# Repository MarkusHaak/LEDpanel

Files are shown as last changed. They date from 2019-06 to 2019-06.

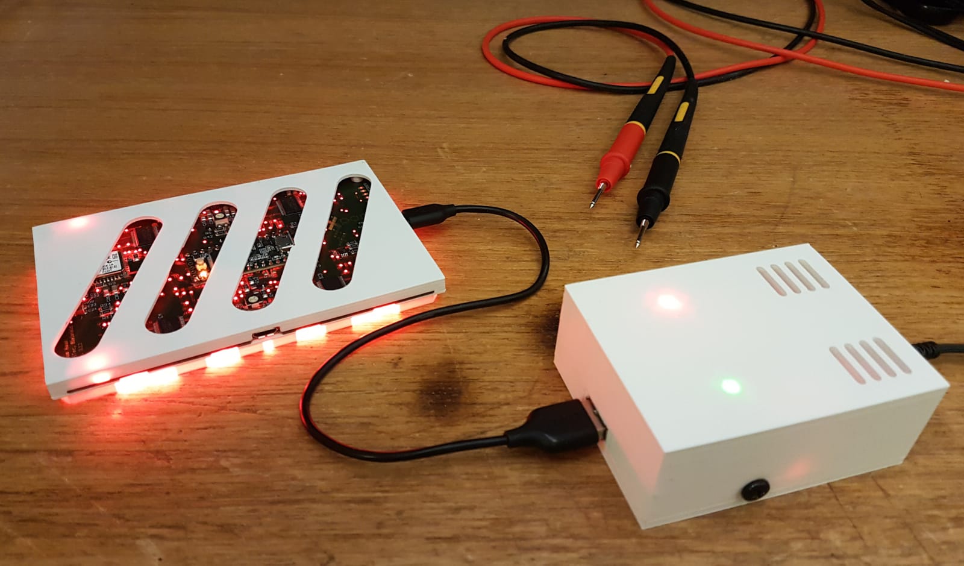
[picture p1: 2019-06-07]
preview/7.jpeg

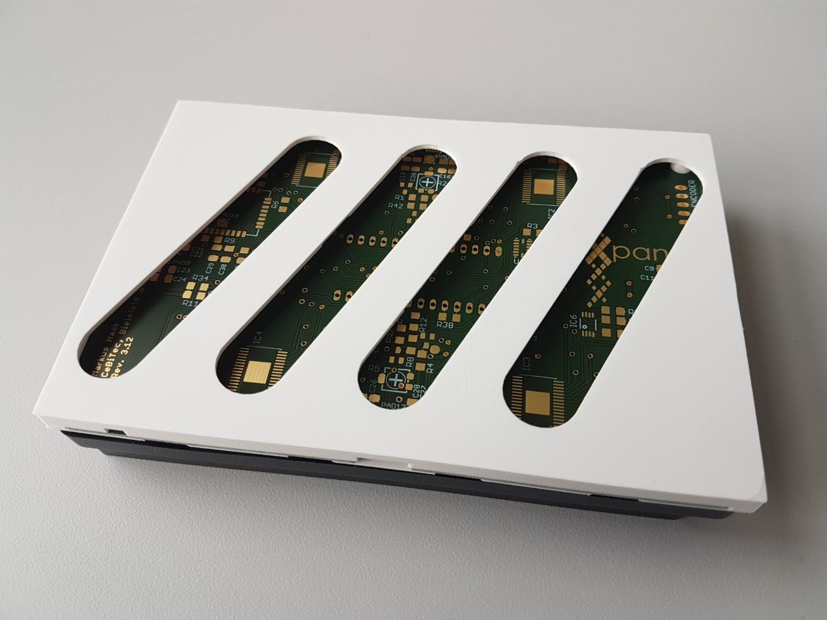
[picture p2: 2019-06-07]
preview/5.jpeg

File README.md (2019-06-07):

# LEDpanel
A multifunctional, bluetooth controlled LED panel for illuminating 96-well microtiter plates containing biological or chemical samples. The first version of this hardware was developed as part of the iGEM project from team Bielefeld CeBiTec 2017. For a detailed description of this first model and its applications in our project, see the [Hardware page](2017.igem.org/Team:Bielefeld-CeBiTec/Hardware) of our project wiki.

## Disclaimer

The hardware described on this github repository is still in prototype phase and both software and hardware may contain design faults. Furthermore, I do not take any responsibility and I am not liable for any damage that is caused by handling of electrical components or devices based on designs, instructions and information in this repository.

## Some Hints for Assembly

This repository is new and there is a lack of documentation. Until I find the time to write a comprehensive instruction for assembly and usage, the following hints are intended to give some orientation.

* In principal, any LEDs can be mounted on the LED panel. The constant current flowing through the LEDs is adjustable with potentiometers on the PCB itself. The LED panel is designed to be configurable to either control the current of all LEDs with a single potentiometer, or two groups of LEDs with an individual potentiometer for each group. Therefore, it is possible to mount two different groups of LEDs on the LED panel. In any case, I highly recommend to adapt the footprint in the PCB design files according to the instructions in the LED's technical sheets.

* Please adapt the file "model_slim_microtiter_adapter.stl" to fit the micro titer plates that are used in your laboratory.

* The parts list is outdated and is probably missing some required parts. Anyways, it might give some orientation in choosing the right parts.

* The LED panel requires two different voltages supplied over a micro usb cable: 3.3 V for the micro controller and logic, and a seperate LED supply voltage that should be at least 0.4 volts above the supply voltage of the LEDs in use. I used two LM2596 based DC-DC voltage regulator boards in a seperate 3d printed case (voltage_regulators_case.stl) to supply the required voltages from a standard 5V DC mains adapter with a barrel connector.

* The LED panel is intended to be controlled over bluetooth via an Android application. Nevertheless, some gpio pins of the teensy are traced to the side of the PCB for optional soldering of pin headers to the PCB that allow the connection of a small LCD screen and a rotary encoder to control basic functionalities of the LED panel. If this is intended, the Arduino code will probably need to be revised. In addition, the 3d printed case needs to be modified accordingly to create space for the display and the rotary encoder.

* The supplied .stl files are solely for illumination of micro titer plates from beneath. For illumination from above a plate, a different 3d printed microtiter adapter needs to be designed.

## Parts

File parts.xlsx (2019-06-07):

class | value | package | distributor | ID | link | # order | p.P. | sum / €
 |  |  |  |  |  |  |  | 0
capacitors | 100n | C1206 | Mouser | 77-VJ1206Y104KXXPBC | https://www.mouser.de/ProductDetail/Vishay-Vitramon/VJ1206Y104KXXPW1BC | 50 | 0.027 | 1.35
 | 10u/16V | C1206 | Mouser | 581-1206ZC106MAT2A | https://www.mouser.de/ProductDetail/AVX/1206ZC106MAT2A | 10 | 0.162 | 1.62
 | 100u/6V3 | C1206 | Mouser | 810-C3216X5R0J107M | https://www.mouser.de/ProductDetail/TDK/C3216X5R0J107M160AB | 10 | 0.845 | 8.45
 |  |  |  |  |  |  |  | 0
pinheaders | female | 18 | Mouser | 437-8018701810001101 | https://www.mouser.de/ProductDetail/Preci-dip/801-87-018-10-001101 | 2 | 1.18 | 2.36
 |  |  |  |  |  |  |  | 0
PWM driver | TLC5947-DAP | HTSSOP32DAP | Mouser | 595-TLC5947DAPR | https://www.mouser.de/ProductDetail/Texas-Instruments/TLC5947DAPR?qs=sGAEpiMZZMsE420DPIasPoaSsRjR8BzZEcbKcRNRsRk%3d | 5 | 2.87 | 14.35
 |  |  |  |  |  |  |  | 0
sensors | MCP9808 | MSOP8 | Mouser | 579-MCP9808T-E/MS | https://www.mouser.de/ProductDetail/Microchip-Technology/MCP9808T-E-MS | 3 | 1.12 | 3.36
 | ADXL345BCCZ | LGA14R80P3X6_300X500X100 | Mouser | 584-ADXL345BCCZ | https://www.mouser.de/ProductDetail/Analog-Devices/ADXL345BCCZ?qs=sGAEpiMZZMvwE4h8i4g3cmpdANGD53Y62K0svRyi38E%3d | 2 | 5.69 | 11.38
 |  |  |  |  |  |  |  | 0
USB | USB3065-XX-00-A_REVE | GCT_USB3065-XX-00-A_REVE | Mouser | 629105136821 | https://www.mouser.de/ProductDetail/Wurth-Electronics/629105136821 | 6 | 1.11 | 6.66
 |  |  |  |  |  |  |  | 0
LED | KPT-1608LVSECK-J3-PRV | KINGBRIGHT_1.6X0.8 | Mouser | APT1608LSECK/J3-PRV | https://www.mouser.de/ProductDetail/Kingbright/APT1608LSECK-J3-PRV | 5 | 0.402 | 2.01
 | KPT-1608LVZGCK | KINGBRIGHT_1.6X0.8 | Mouser | APT1608LZGCK | https://www.mouser.de/ProductDetail/Kingbright/APT1608LZGCK | 5 | 0.41 | 2.05
 | VLMU1610-365-135 | PLCC-2 | Mouser | 78-VLMR333U1AA-GS08 | https://www.mouser.de/ProductDetail/Vishay-Semiconductors/VLMR333U1AA-GS08 | 130 | 0.305 | 39.65
 |  |  |  |  |  |  |  | 0
transistors | BC807-16SMD | SOT23-BEC | Mouser | 863-BC807-25LT3G | https://www.mouser.de/ProductDetail/ON-Semiconductor/BC807-25LT3G | 3 | 0.098 | 0.294
 |  |  |  |  |  |  |  | 0
resistors | 1K | R1206 | Mouser | 71-RCG12061K00FKEA | https://www.mouser.de/ProductDetail/Vishay-Draloric/RCG12061K00FKEA | 10 | 0.082 | 0.82
 | 10K | R1206 | Mouser | 71-RCG120610K0FKEA | https://www.mouser.de/ProductDetail/Vishay-Draloric/RCG120610K0FKEA | 15 | 0.082 | 1.23
 | 4K7 | R1206 | Mouser | 71-RCG12064K70JNEA | https://www.mouser.de/ProductDetail/Vishay-Draloric/RCG12064K70JNEA | 5 | 0.082 | 0.41
 | 0R | R1206 | Mouser | 71-RCG12060000Z0EA | https://www.mouser.de/ProductDetail/Vishay-Draloric/RCG12060000Z0EA | 15 | 0.082 | 1.23
 | 750R | R1206 | Mouser | 603-RC1206FR-07750RL | https://www.mouser.de/ProductDetail/Yageo/RC1206FR-07750RL | 10 | 0.02 | 0.2
 | 330R | R1206 | Mouser | 603-RC1206FR-07330RL | https://www.mouser.de/ProductDetail/Yageo/RC1206FR-07330RL?qs=sGAEpiMZZMvdGkrng054t8AJgcdMkx7xi3kA7AOJ26Y%3d | 10 | 0.02 | 0.2
 | 5K TRIMM | RTRIM4G/J | Mouser | 72-TS53YJ-5K | https://www.mouser.de/ProductDetail/Vishay-Sfernice/TS53YJ502MR10 | 4 | 1.06 | 4.24
 |  |  |  |  |  |  |  | 0
bluetooth | BLUETOOTH-RN-41" | RN41 | Mouser | 765-RN-41 | https://www.mouser.de/ProductDetail/Microchip-Technology/RN41-I-RM?qs=sGAEpiMZZMtqO%252bWUGLBzeMW4TCGBne5E | 1 | 21.35 | 21.35
 |  |  |  |  |  |  |  | 0
microcontroller | teensy3.2 |  | Mouser | 474-DEV-13736 | https://www.mouser.de/ProductDetail/SparkFun/DEV-13736 | 1 | 19.19 | 19.19
 |  |  |  |  |  |  |  | 0
PCB | PCB 127.76 x 85,48 |  | BETA Layout |  | https://de.beta-layout.com/leiterplatten/konfigurator/ | 1 | 84.9 | 84.9
 |  |  |  |  |  |  |  | 0
3D printing filament | PLA 1.75mm white |  | Conrad | 1093139 | https://www.conrad.de/de/filament-renkforce-pla-175-mm-weiss-1-kg-1093139.html | 1 | 32.99 | 32.99
 |  |  |  |  |  |  |  | 0
voltage regulators | LM2596 (or equivalent) DC DC voltage regulator boards |  | amazon |  | https://www.amazon.de/WINOMO-1-23-30V-DC-Einstellbare-Spannung-Konverter/dp/B01B7EEWGK?__mk_de_DE=%C3%85M%C3%85%C5%BD%C3%95%C3%91&s=gateway | 5 |  | 12.39

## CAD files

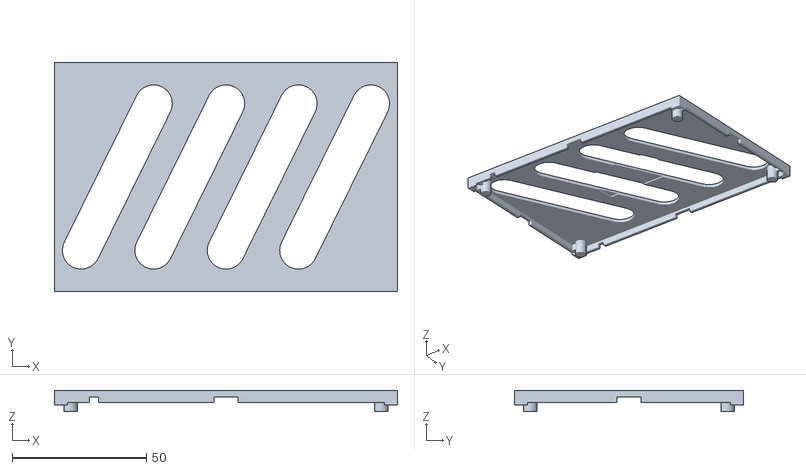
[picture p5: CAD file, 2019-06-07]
case/model_slim_lower_case.stl
127.8 x 85.5 x 8.00

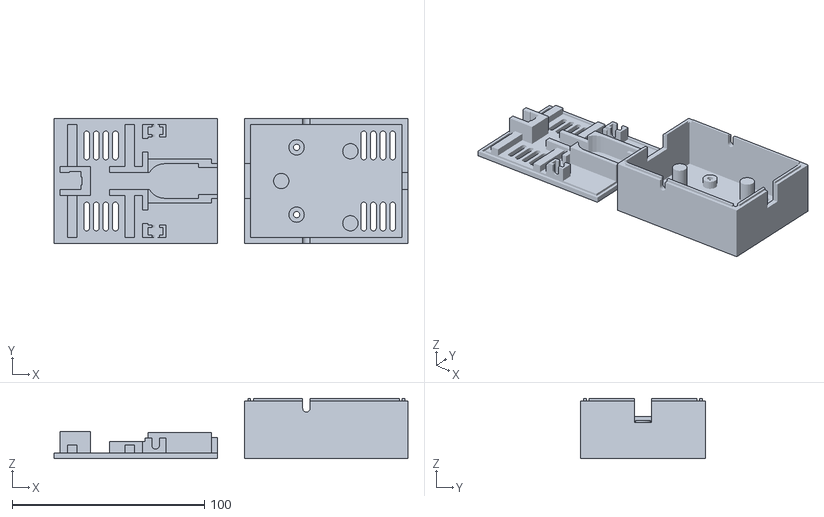
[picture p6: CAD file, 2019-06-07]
case/voltage_regulators_case.stl
184.3 x 65.0 x 31.3

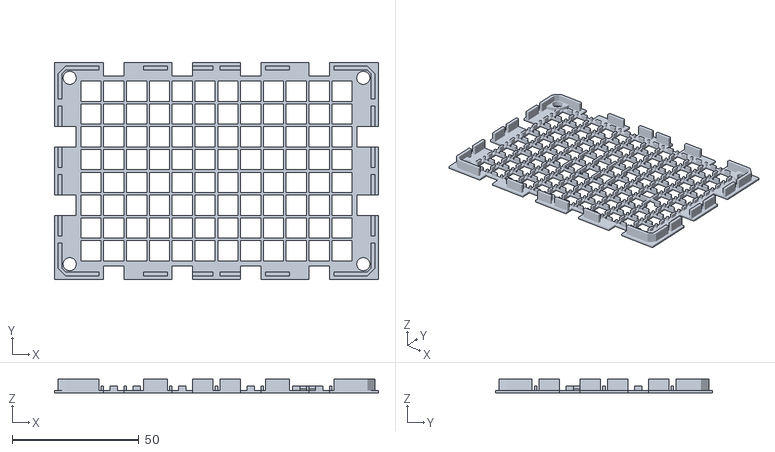
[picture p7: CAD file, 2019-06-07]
case/model_slim_microtiter_adapter.stl
127.8 x 85.5 x 5.50

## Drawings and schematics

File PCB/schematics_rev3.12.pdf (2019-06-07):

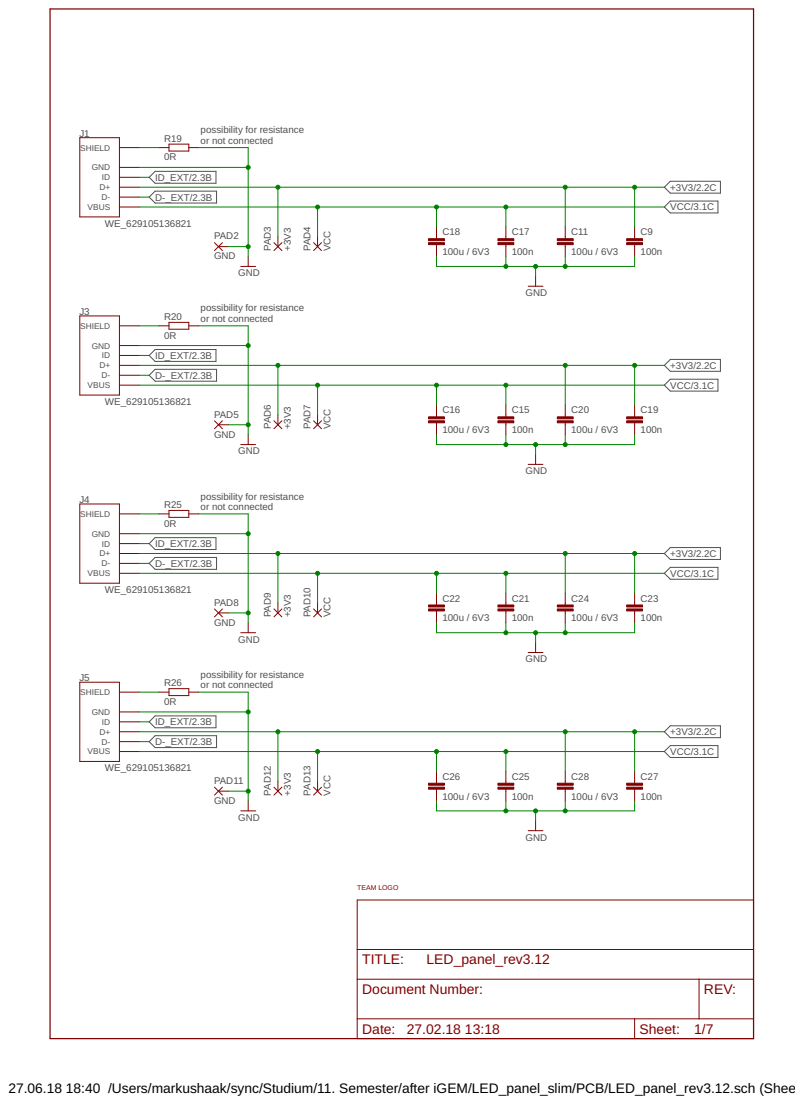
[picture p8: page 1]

Document Number: | REV:

Date: 27.02.18 13:18 | Sheet: 1/7

27.06.18 18:40 /Users/markushaak/sync/Studium/11. Semester/after iGEM/LED_panel_slim/PCB/LED_panel_rev3.12.sch (Sheet: 1/7)

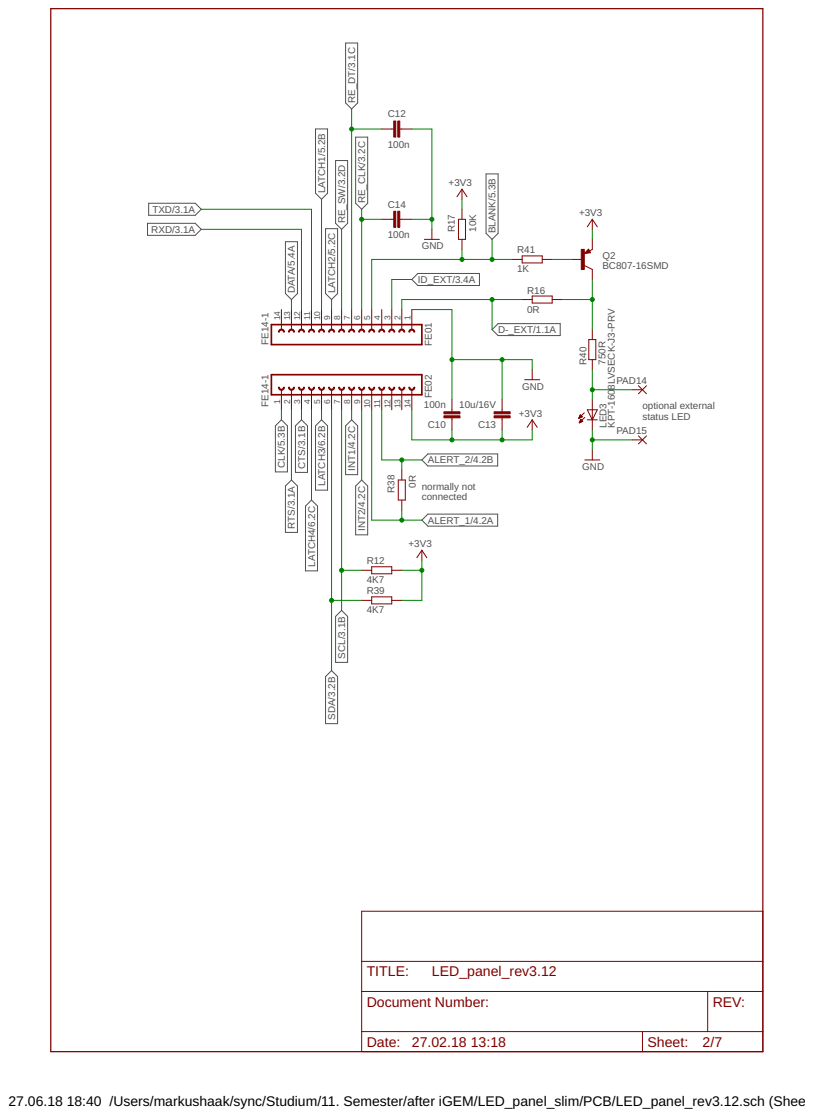
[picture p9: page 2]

optional external status LED

27.06.18 18:40 /Users/markushaak/sync/Studium/11. Semester/after iGEM/LED_panel_slim/PCB/LED_panel_rev3.12.sch (Sheet: 2/7)

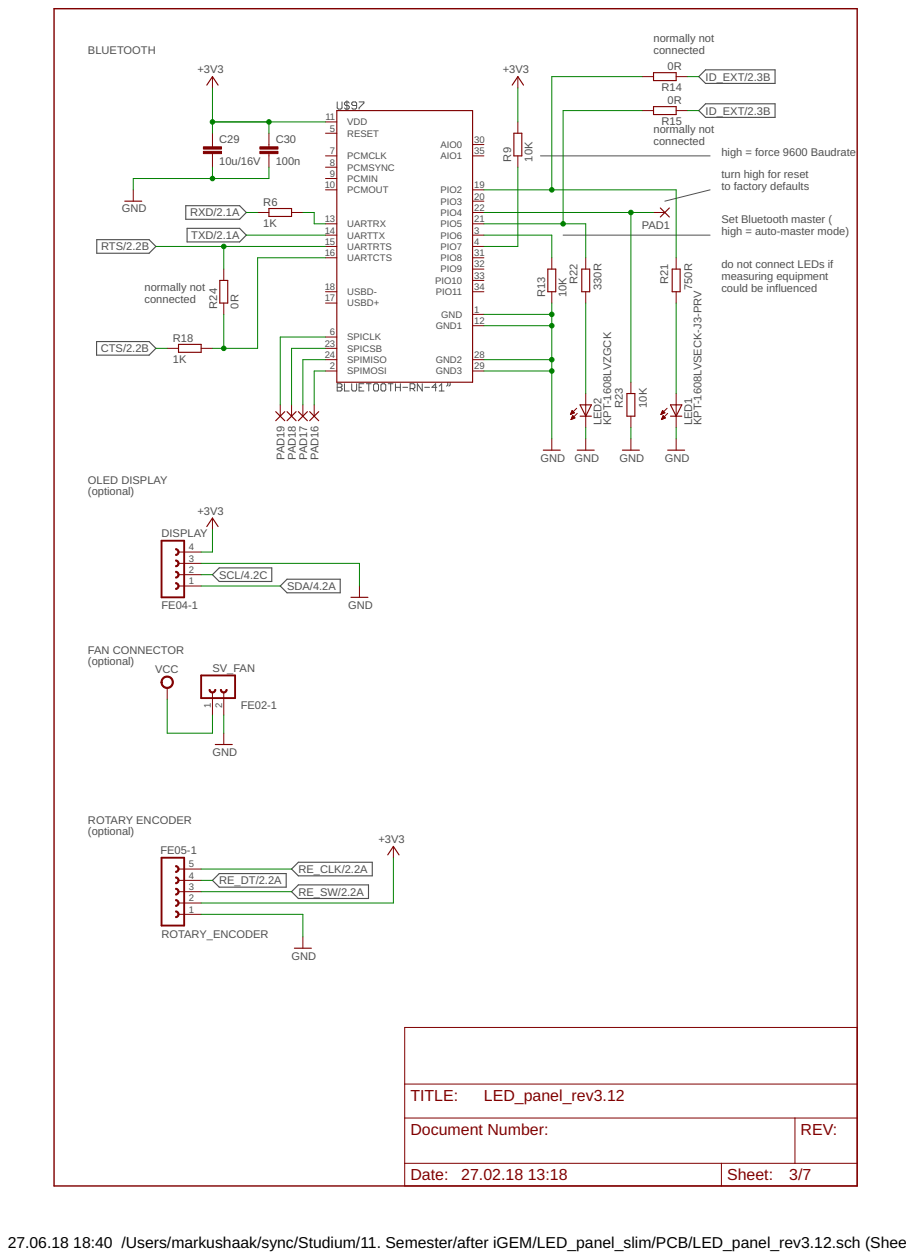
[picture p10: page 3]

high = force 9600 Baudrate
turn high for reset
to factory defaults Set Bluetooth master (

high = auto-master mode)

do not connect LEDs if measuring equipment could be influenced

27.06.18 18:40 /Users/markushaak/sync/Studium/11. Semester/after iGEM/LED_panel_slim/PCB/LED_panel_rev3.12.sch (Sheet: 3/7)

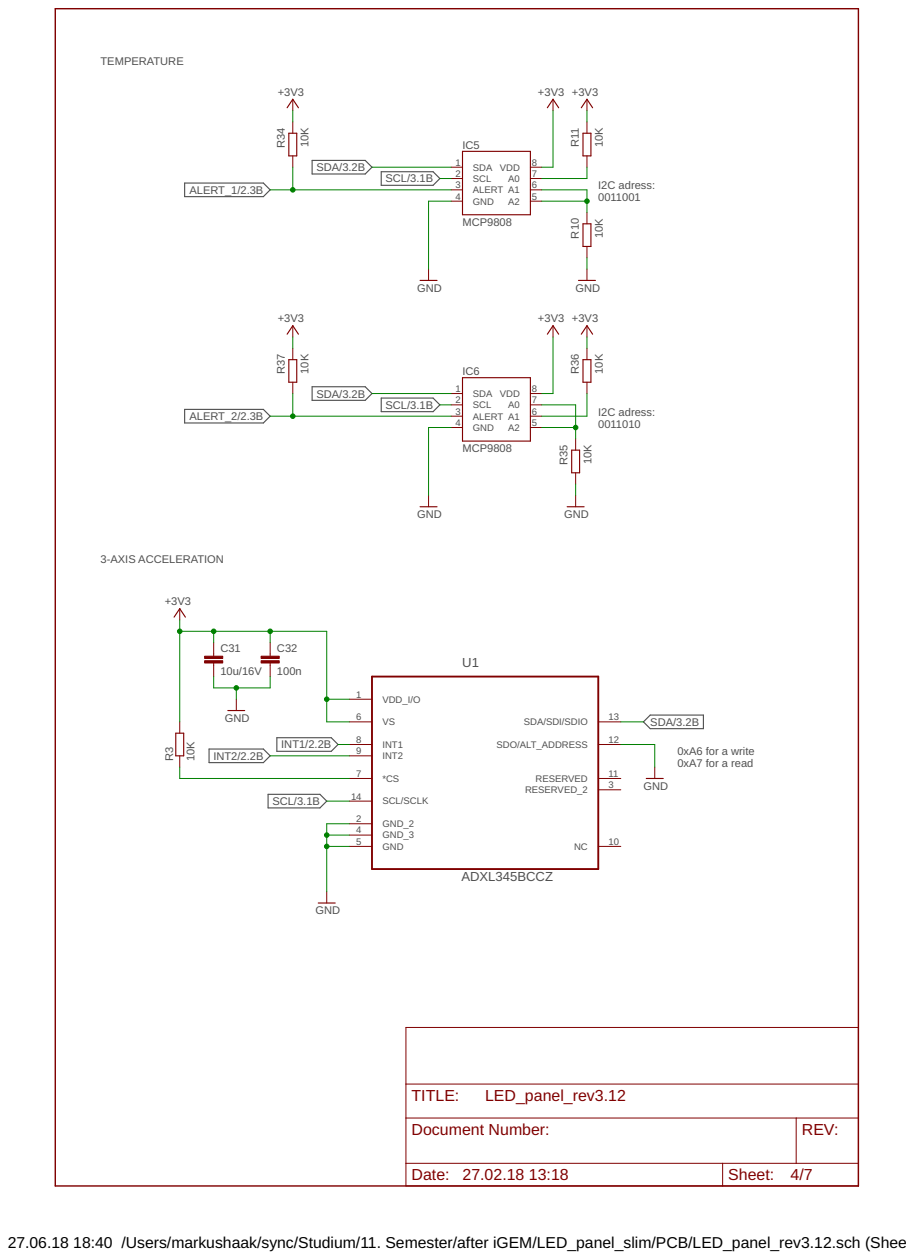
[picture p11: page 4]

27.06.18 18:40 /Users/markushaak/sync/Studium/11. Semester/after iGEM/LED_panel_slim/PCB/LED_panel_rev3.12.sch (Sheet: 4/7)

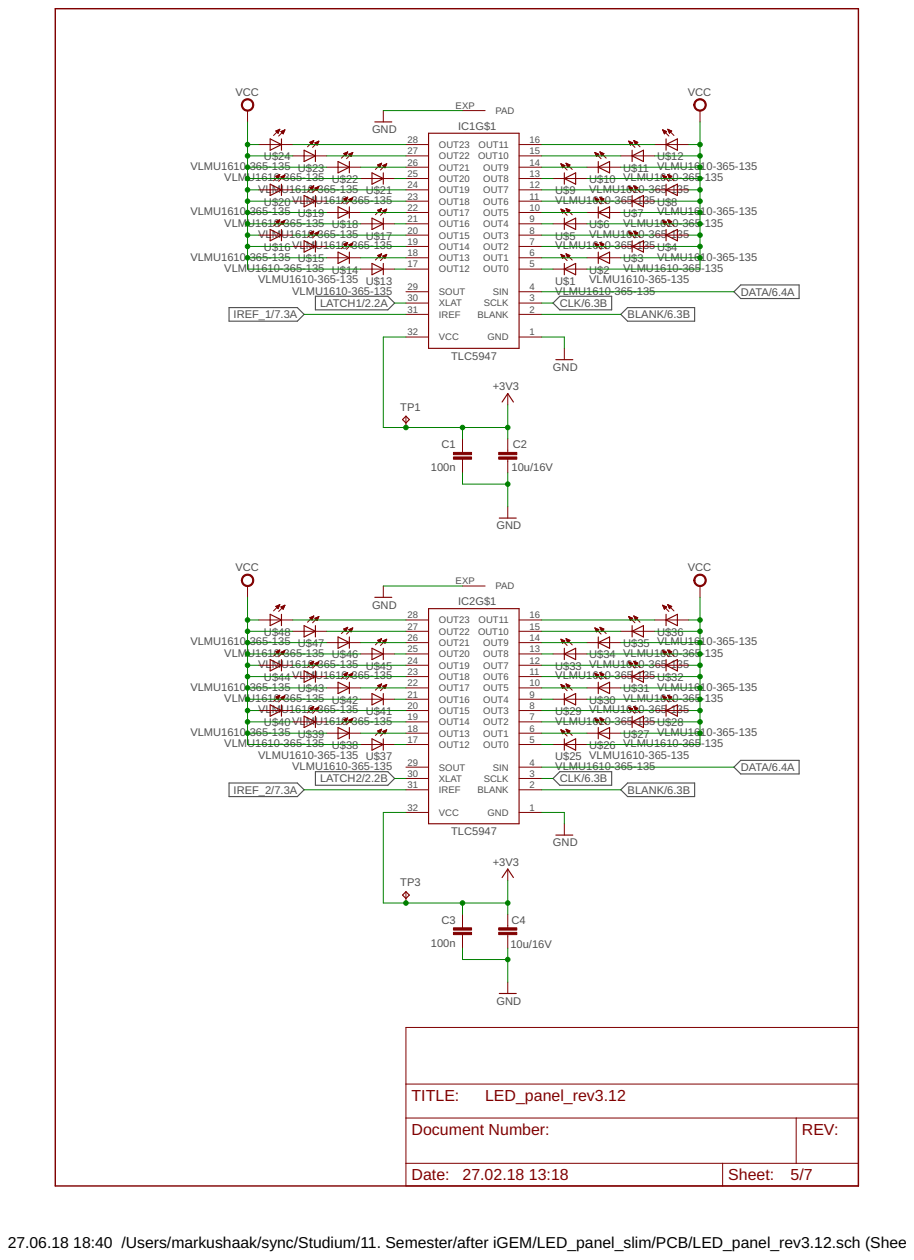
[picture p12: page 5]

20 VLMU1610-365-135 U$17 | 8 OUT4 U$5 VLMU1610-365-135

27.06.18 18:40 /Users/markushaak/sync/Studium/11. Semester/after iGEM/LED_panel_slim/PCB/LED_panel_rev3.12.sch (Sheet: 5/7)

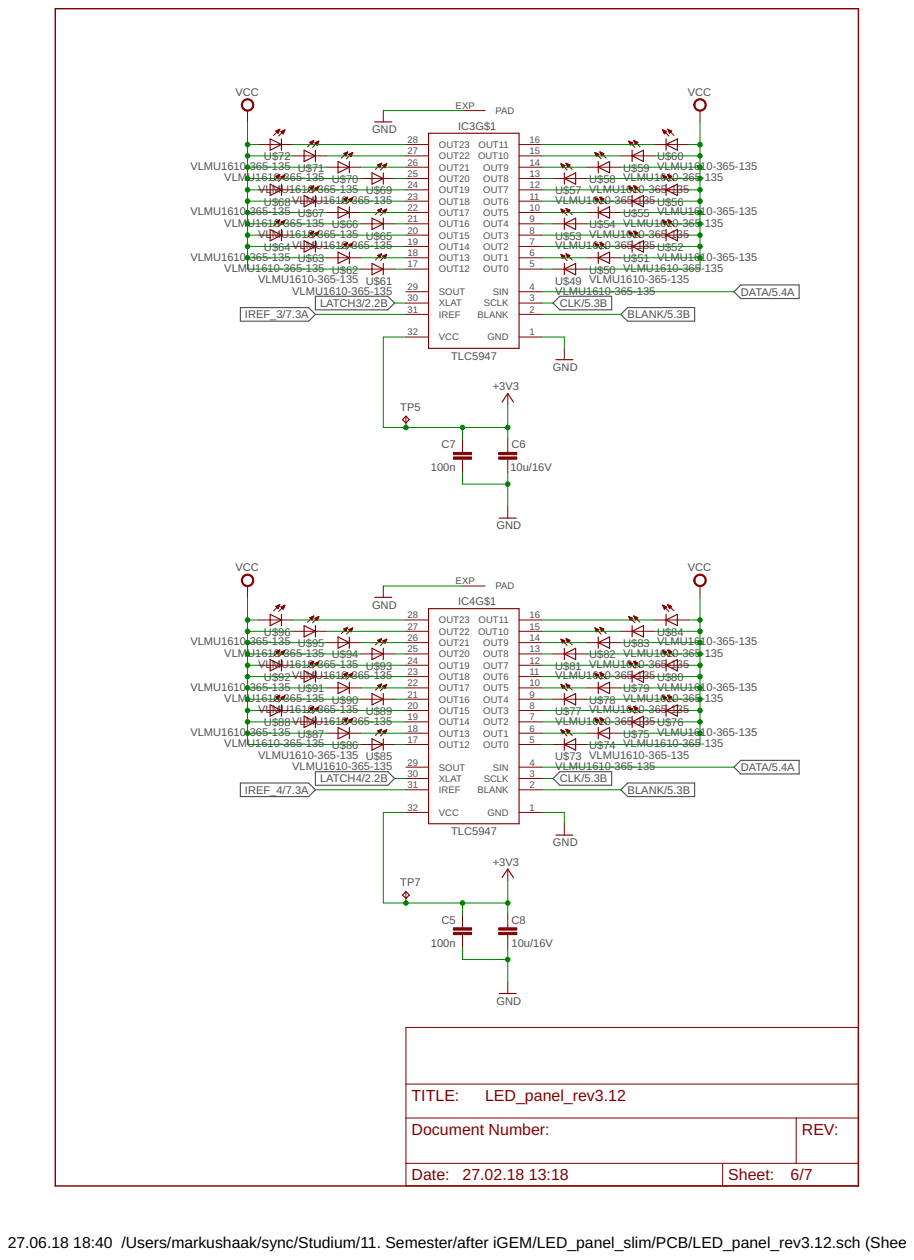
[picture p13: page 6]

20 VLMU1610-365-135 U$65 | 8 OUT4 U$53 VLMU1610-365-135

27.06.18 18:40 /Users/markushaak/sync/Studium/11. Semester/after iGEM/LED_panel_slim/PCB/LED_panel_rev3.12.sch (Sheet: 6/7)

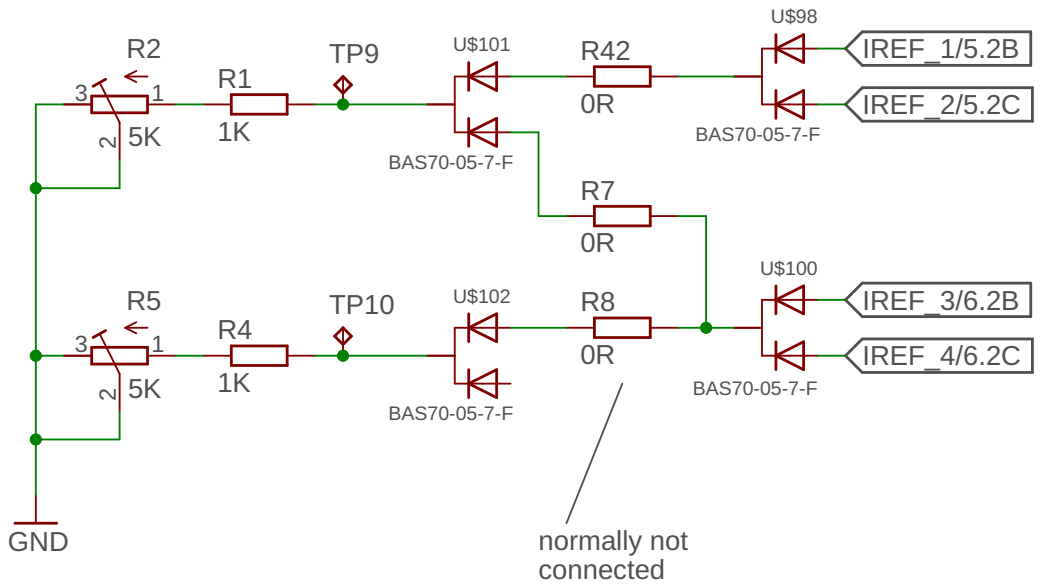
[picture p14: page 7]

27.06.18 18:40 /Users/markushaak/sync/Studium/11. Semester/after iGEM/LED_panel_slim/PCB/LED_panel_rev3.12.sch (Sheet: 7/7)

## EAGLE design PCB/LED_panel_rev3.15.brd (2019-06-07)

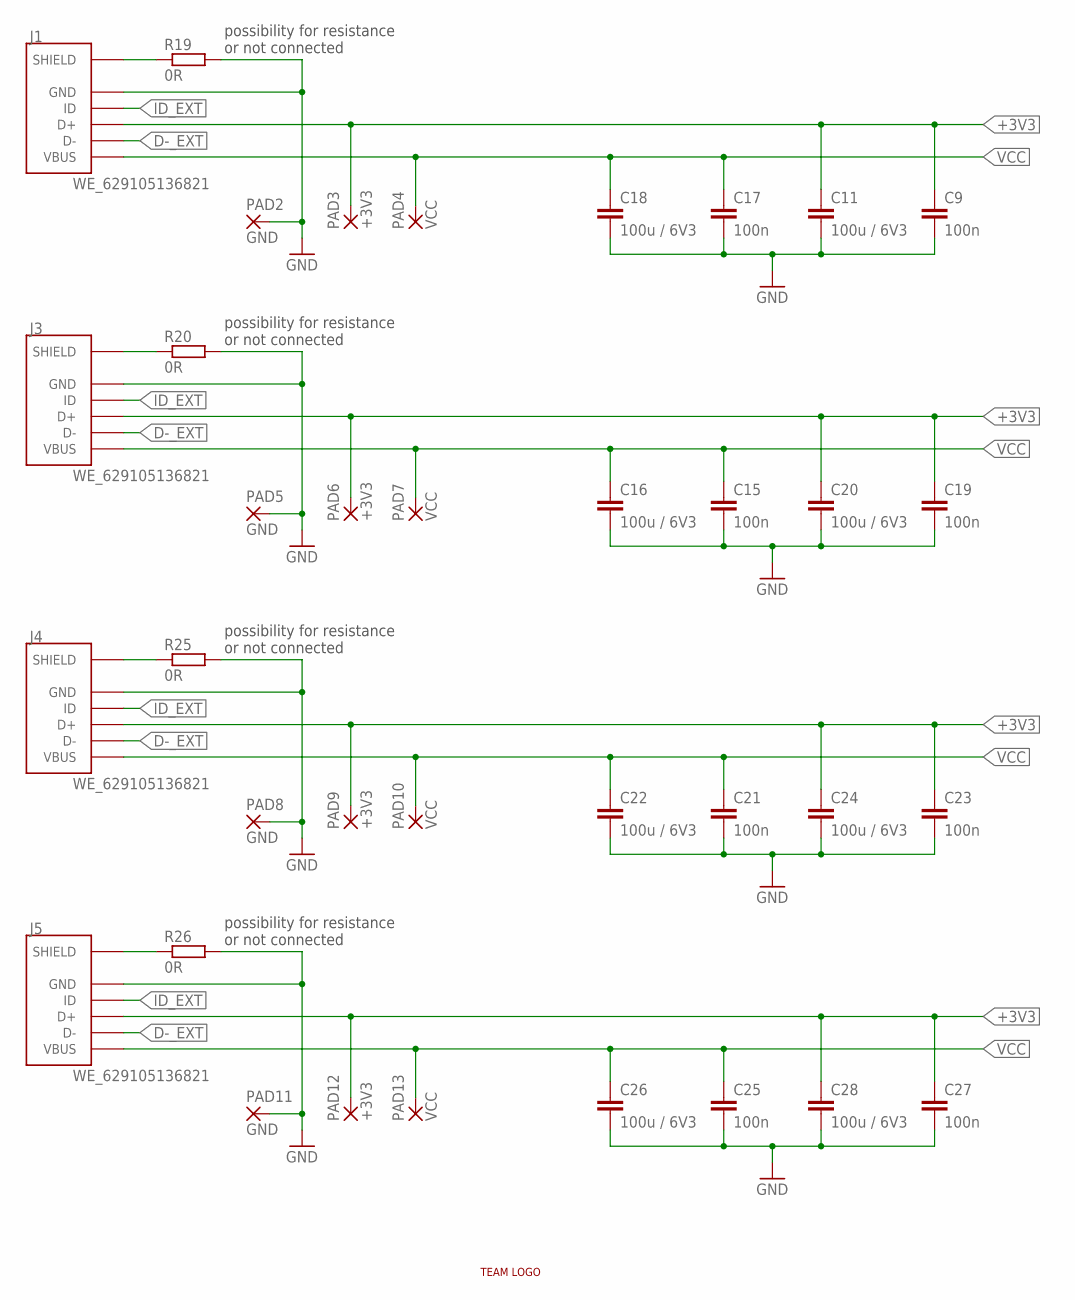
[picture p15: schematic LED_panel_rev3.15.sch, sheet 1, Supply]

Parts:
C9, C15, C17, C19, C21, C23, C25, C27: 100n; C1206K
C11, C16, C18, C20, C22, C24, C26, C28: 100u / 6V3; C1206K
J1, J3, J4, J5: WE_629105136821; 629105136821
PAD2, PAD5, PAD8, PAD11: GND; 2,54/1,0
PAD3, PAD6, PAD9, PAD12: +3V3; 2,54/1,0
PAD4, PAD7, PAD10, PAD13: VCC; 2,54/1,0
R19, R20, R25, R26: 0R; R1206
U$99: LOGO_RESTRICT

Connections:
+3V3: C9.1, C11.1, C19.1, C20.1, C23.1, C24.1, C27.1, C28.1, J1.3 (D+), J3.3 (D+), J4.3 (D+), J5.3 (D+), PAD3.1, PAD6.1, PAD9.1, PAD12.1; also elsewhere on the board
D-_EXT: J1.2 (D-), J3.2 (D-), J4.2 (D-), J5.2 (D-); also elsewhere on the board
GND: C9.2, C11.2, C15.2, C16.2, C17.2, C18.2, C19.2, C20.2, C21.2, C22.2, C23.2, C24.2, C25.2, C26.2, C27.2, C28.2, J1.5 (GND), J3.5 (GND), J4.5 (GND), J5.5 (GND), PAD2.1, PAD5.1, PAD8.1, PAD11.1, R19.2, R20.2, R25.2, R26.2; also elsewhere on the board
ID_EXT: J1.4 (ID), J3.4 (ID), J4.4 (ID), J5.4 (ID); also elsewhere on the board
SHIELD1: J1.6 (SHIELD), J1.7 (SHIELD), J1.8 (SHIELD), J1.9 (SHIELD), R19.1
SHIELD3: J3.6 (SHIELD), J3.7 (SHIELD), J3.8 (SHIELD), J3.9 (SHIELD), R20.1
SHIELD4: J4.6 (SHIELD), J4.7 (SHIELD), J4.8 (SHIELD), J4.9 (SHIELD), R25.1
SHIELD5: J5.6 (SHIELD), J5.7 (SHIELD), J5.8 (SHIELD), J5.9 (SHIELD), R26.1
VCC: C15.1, C16.1, C17.1, C18.1, C21.1, C22.1, C25.1, C26.1, J1.1 (VBUS), J3.1 (VBUS), J4.1 (VBUS), J5.1 (VBUS), PAD4.1, PAD7.1, PAD10.1, PAD13.1; also elsewhere on the board

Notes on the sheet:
possibility for resistance or not connected

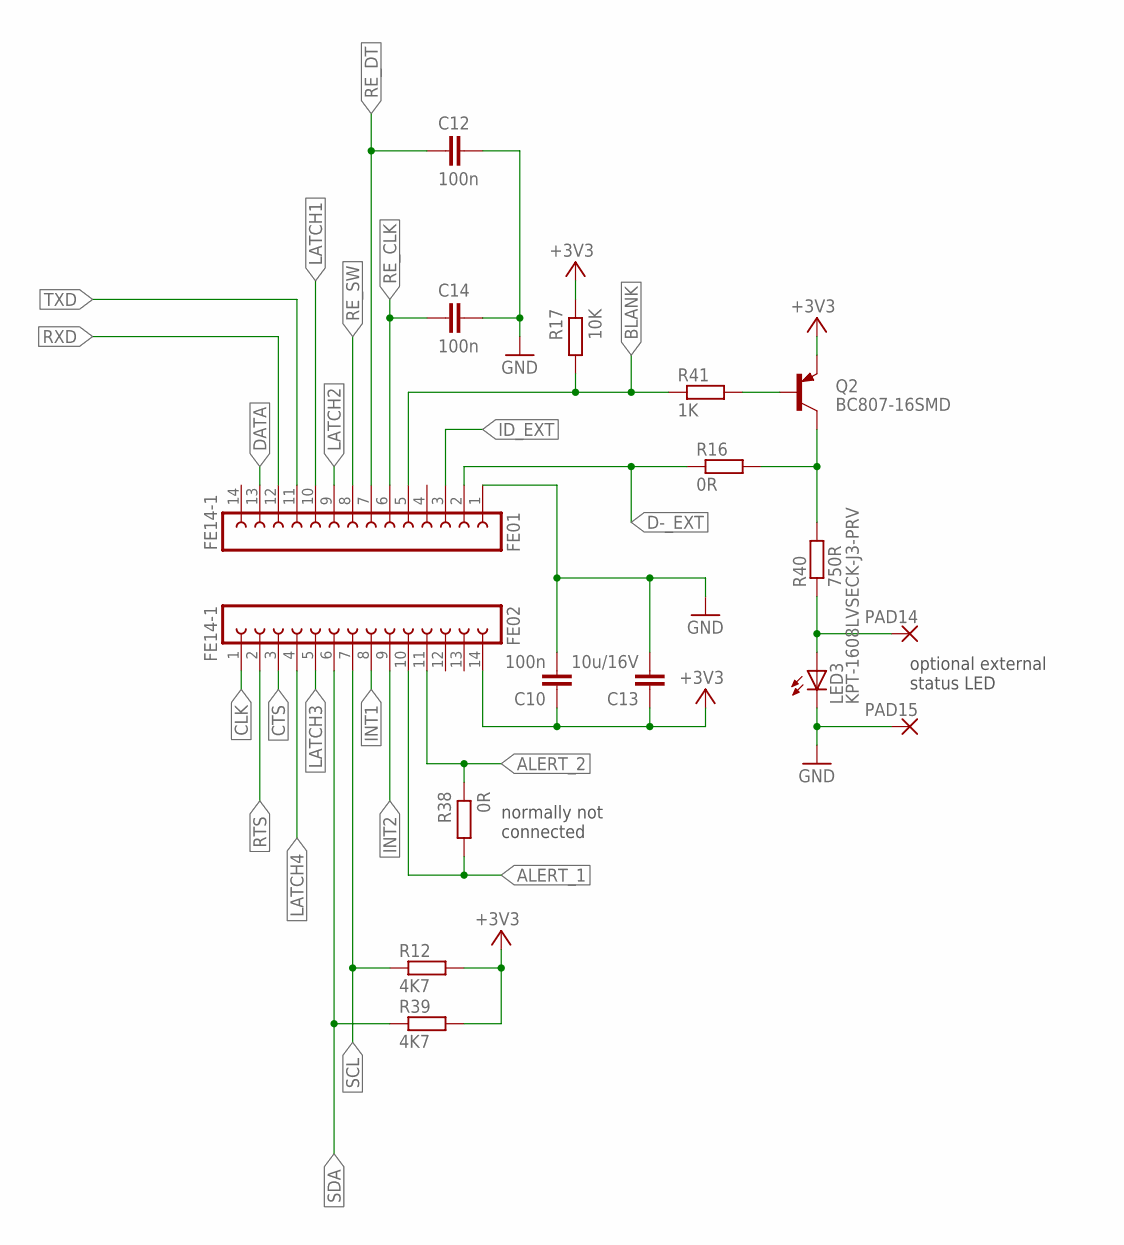
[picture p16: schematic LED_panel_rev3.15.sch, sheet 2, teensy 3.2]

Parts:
C10, C12, C14: 100n; C1206K
C13: 10u/16V; C1206K
FE01, FE02: FE14-1; FE14
LED3: KPT-1608LVSECK-J3-PRV; MH_KINGBRIGHT_1.6X0.8
PAD14, PAD15: 2,54/1,0
Q2: BC807-16SMD; SOT23-BEC
R12, R39: 4K7; R1206
R16, R38: 0R; R1206
R17: 10K; R1206
R40: 750R; R1206
R41: 1K; R1206

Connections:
+3V3: C10.1, C13.1, FE02.14, Q2.E, R12.2, R17.1, R39.2; also elsewhere on the board
ALERT_1: FE02.10, R38.2; also elsewhere on the board
ALERT_2: FE02.11, R38.1; also elsewhere on the board
BLANK: FE01.5, R17.2, R41.1; also elsewhere on the board
CLK: FE02.1; also elsewhere on the board
CTS: FE02.3; also elsewhere on the board
D-_EXT: FE01.2, R16.1; also elsewhere on the board
DATA: FE01.13; also elsewhere on the board
GND: C10.2, C12.1, C13.2, C14.1, FE01.1, LED3.C, PAD15.1; also elsewhere on the board
ID_EXT: FE01.3; also elsewhere on the board
INT1: FE02.8; also elsewhere on the board
INT2: FE02.9; also elsewhere on the board
LATCH1: FE01.10; also elsewhere on the board
LATCH2: FE01.9; also elsewhere on the board
LATCH3: FE02.5; also elsewhere on the board
LATCH4: FE02.4; also elsewhere on the board
unnamed: Q2.B, R41.2
unnamed: Q2.C, R16.2, R40.2
unnamed: LED3.A, PAD14.1, R40.1
RE_CLK: C14.2, FE01.6; also elsewhere on the board
RE_DT: C12.2, FE01.7; also elsewhere on the board
RE_SW: FE01.8; also elsewhere on the board
RTS: FE02.2; also elsewhere on the board
RXD: FE01.12; also elsewhere on the board
SCL: FE02.7, R12.1; also elsewhere on the board
SDA: FE02.6, R39.1; also elsewhere on the board
TXD: FE01.11; also elsewhere on the board

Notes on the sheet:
normally not connected
optional external status LED

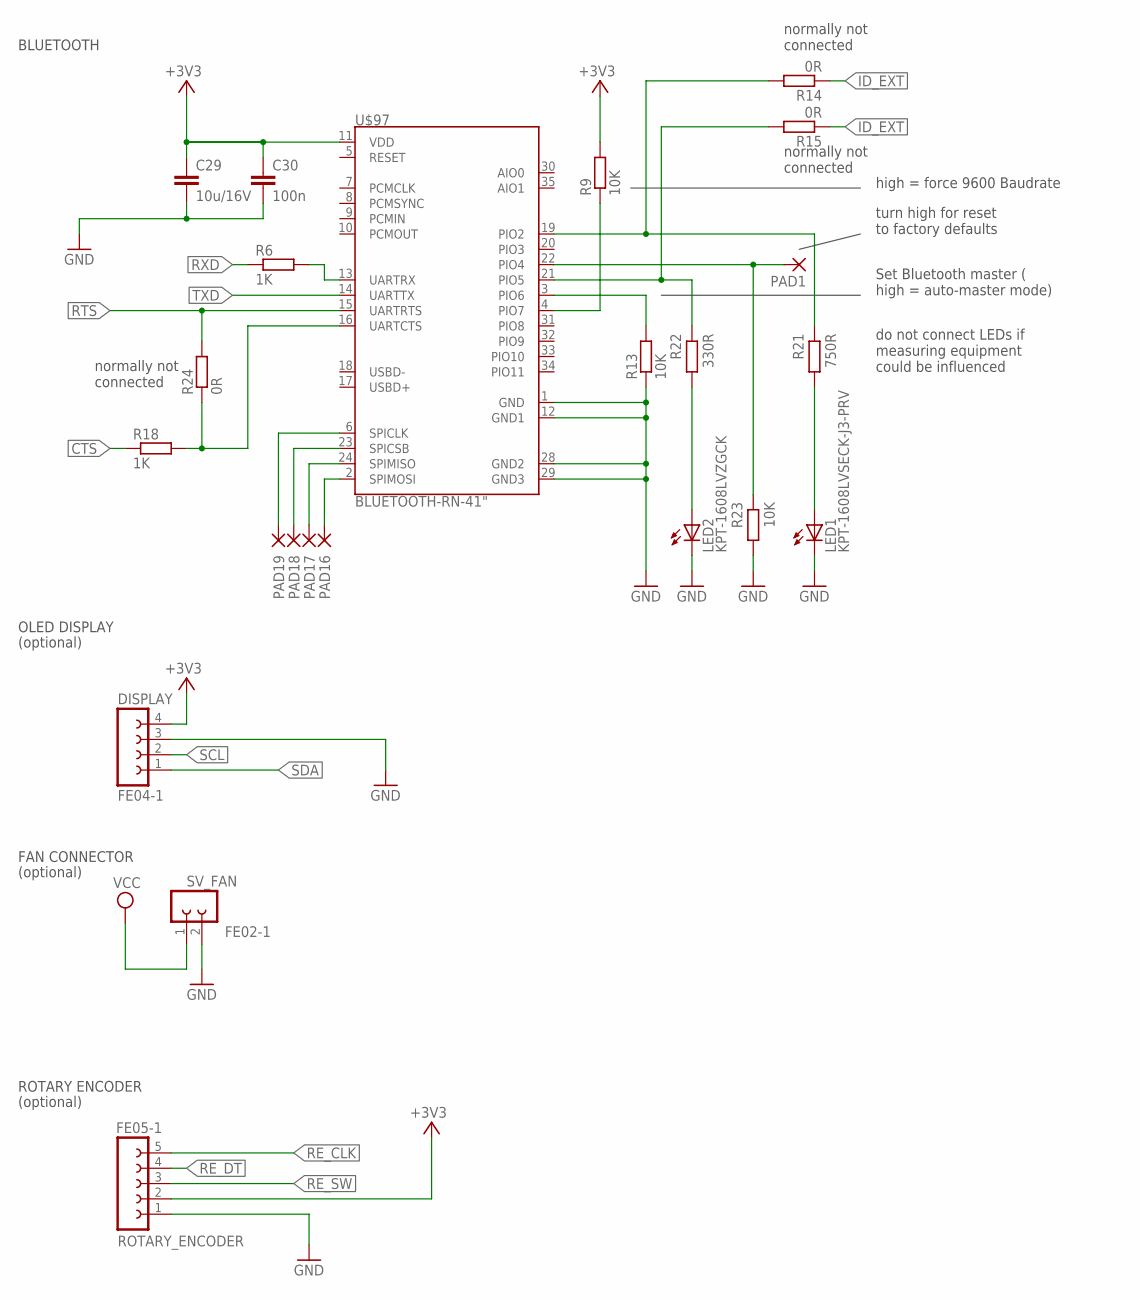
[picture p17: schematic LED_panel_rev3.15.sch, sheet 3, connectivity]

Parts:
C29: 10u/16V; C1206K
C30: 100n; C1206K
DISPLAY: FE04-1; FE04
LED1: KPT-1608LVSECK-J3-PRV; MH_KINGBRIGHT_1.6X0.8
LED2: KPT-1608LVZGCK; MH_KINGBRIGHT_1.6X0.8
PAD1, PAD16, PAD17, PAD18, PAD19: 2,54/1,0
R6, R18: 1K; R1206
R9, R13, R23: 10K; R1206
R14, R15, R24: 0R; R1206
R21: 750R; R1206
R22: 330R; R1206
ROTARY_ENCODER: FE05-1; FE05
SV_FAN: FE02-1; FE02
U$97: BLUETOOTH-RN-41"; RN41

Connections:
+3V3: C29.1, C30.1, DISPLAY.4, R9.2, ROTARY_ENCODER.2, U$97.11 (VDD); also elsewhere on the board
CTS: R18.1; also elsewhere on the board
GND: C29.2, C30.2, DISPLAY.3, LED1.C, LED2.C, R13.1, R23.2, ROTARY_ENCODER.1, SV_FAN.2, U$97.1 (GND), U$97.12 (GND1), U$97.28 (GND2), U$97.29 (GND3); also elsewhere on the board
ID_EXT: R14.1, R15.1; also elsewhere on the board
unnamed: R9.1, U$97.4 (PIO7)
unnamed: R13.2, U$97.3 (PIO6)
unnamed: R18.2, R24.1, U$97.16 (UARTCTS)
unnamed: PAD16.1, U$97.2 (SPIMOSI)
unnamed: PAD17.1, U$97.24 (SPIMISO)
unnamed: R6.2, U$97.13 (UARTRX)
unnamed: PAD18.1, U$97.23 (SPICSB)
unnamed: R15.2, R22.1, U$97.21 (PIO5)
unnamed: LED2.A, R22.2
unnamed: PAD19.1, U$97.6 (SPICLK)
unnamed: LED1.A, R21.2
unnamed: R14.2, R21.1, U$97.19 (PIO2)
PIO4: PAD1.1, R23.1, U$97.22 (PIO4)
RE_CLK: ROTARY_ENCODER.5; also elsewhere on the board
RE_DT: ROTARY_ENCODER.4; also elsewhere on the board
RE_SW: ROTARY_ENCODER.3; also elsewhere on the board
RTS: R24.2, U$97.15 (UARTRTS); also elsewhere on the board
RXD: R6.1; also elsewhere on the board
SCL: DISPLAY.2; also elsewhere on the board
SDA: DISPLAY.1; also elsewhere on the board
TXD: U$97.14 (UARTTX); also elsewhere on the board
VCC: SV_FAN.1; also elsewhere on the board

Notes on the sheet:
normally not connected
OLED DISPLAY
ROTARY ENCODER
BLUETOOTH
FAN CONNECTOR
do not connect LEDs if measuring equipment could be influenced
(optional)
high = force 9600 Baudrate
turn high for reset to factory defaults
Set Bluetooth master ( high = auto-master mode)

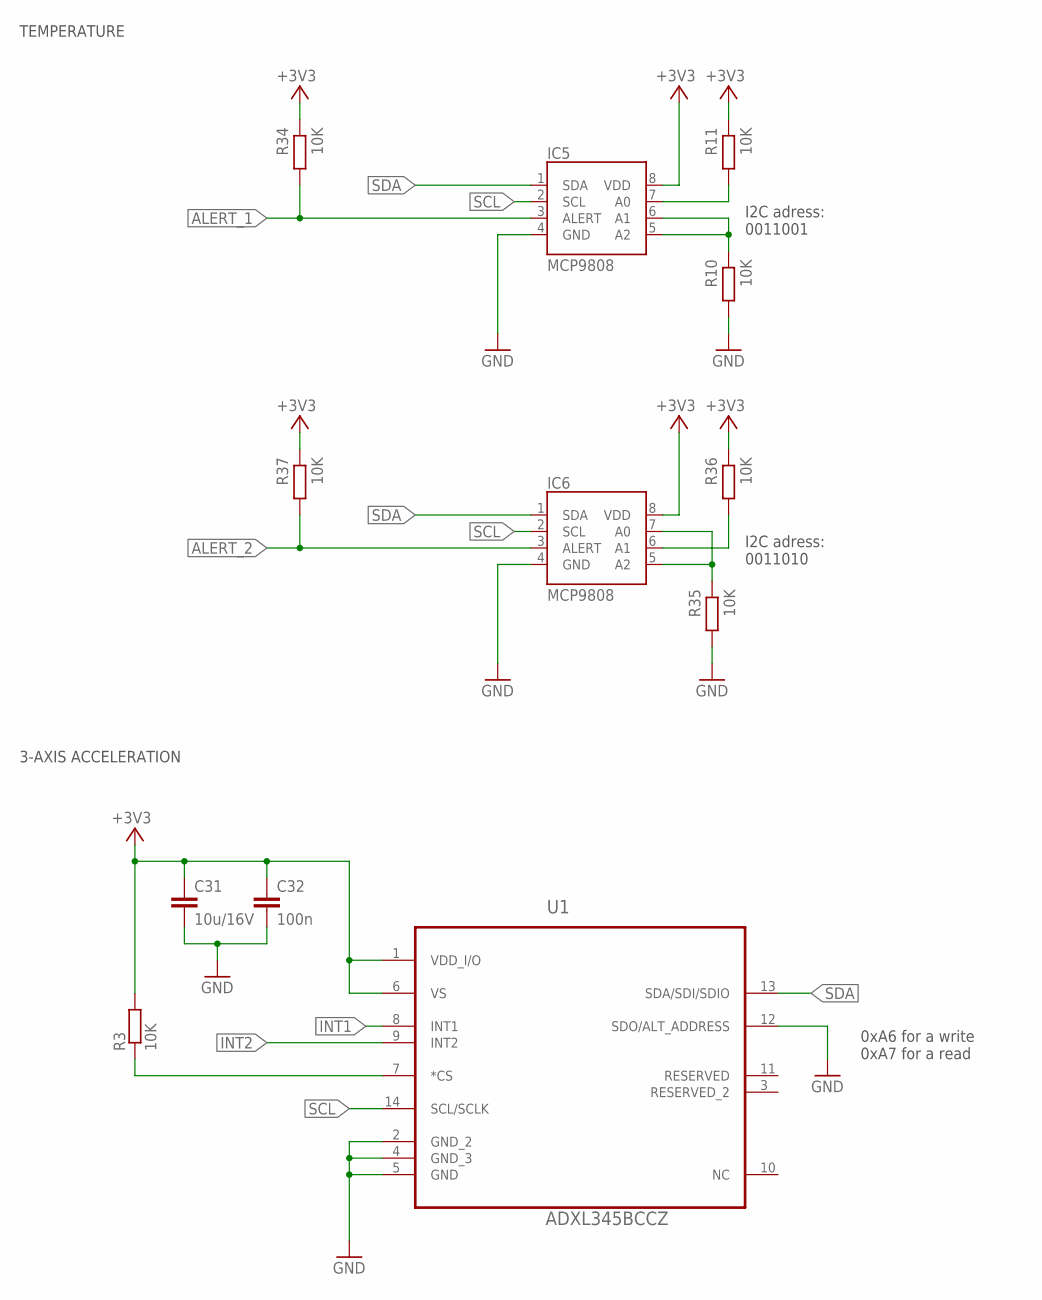
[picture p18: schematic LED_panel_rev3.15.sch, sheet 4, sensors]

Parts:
C31: 10u/16V; C1206K
C32: 100n; C1206K
IC5, IC6: MCP9808; MSOP8
R3, R10, R11, R34, R35, R36, R37: 10K; R1206
U1: ADXL345BCCZ; LGA14R80P3X6_300X500X100

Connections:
+3V3: C31.1, C32.1, IC5.8 (VDD), IC6.8 (VDD), R3.2, R11.1, R34.1, R36.1, R37.1, U1.1 (VDD_I/O), U1.6 (VS); also elsewhere on the board
ALERT_1: IC5.3 (ALERT), R34.2; also elsewhere on the board
ALERT_2: IC6.3 (ALERT), R37.2; also elsewhere on the board
GND: C31.2, C32.2, IC5.4 (GND), IC6.4 (GND), R10.2, R35.2, U1.2 (GND_2), U1.4 (GND_3), U1.5 (GND), U1.12 (SDO/ALT_ADDRESS); also elsewhere on the board
INT1: U1.8 (INT1); also elsewhere on the board
INT2: U1.9 (INT2); also elsewhere on the board
unnamed: IC5.5 (A2), IC5.6 (A1), R10.1
unnamed: IC5.7 (A0), R11.2
unnamed: IC6.5 (A2), IC6.7 (A0), R35.1
unnamed: R3.1, U1.7 (*CS)
unnamed: IC6.6 (A1), R36.2
SCL: IC5.2 (SCL), IC6.2 (SCL), U1.14 (SCL/SCLK); also elsewhere on the board
SDA: IC5.1 (SDA), IC6.1 (SDA), U1.13 (SDA/SDI/SDIO); also elsewhere on the board

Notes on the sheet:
TEMPERATURE
I2C adress: 0011001
I2C adress: 0011010
3-AXIS ACCELERATION
0xA6 for a write 0xA7 for a read

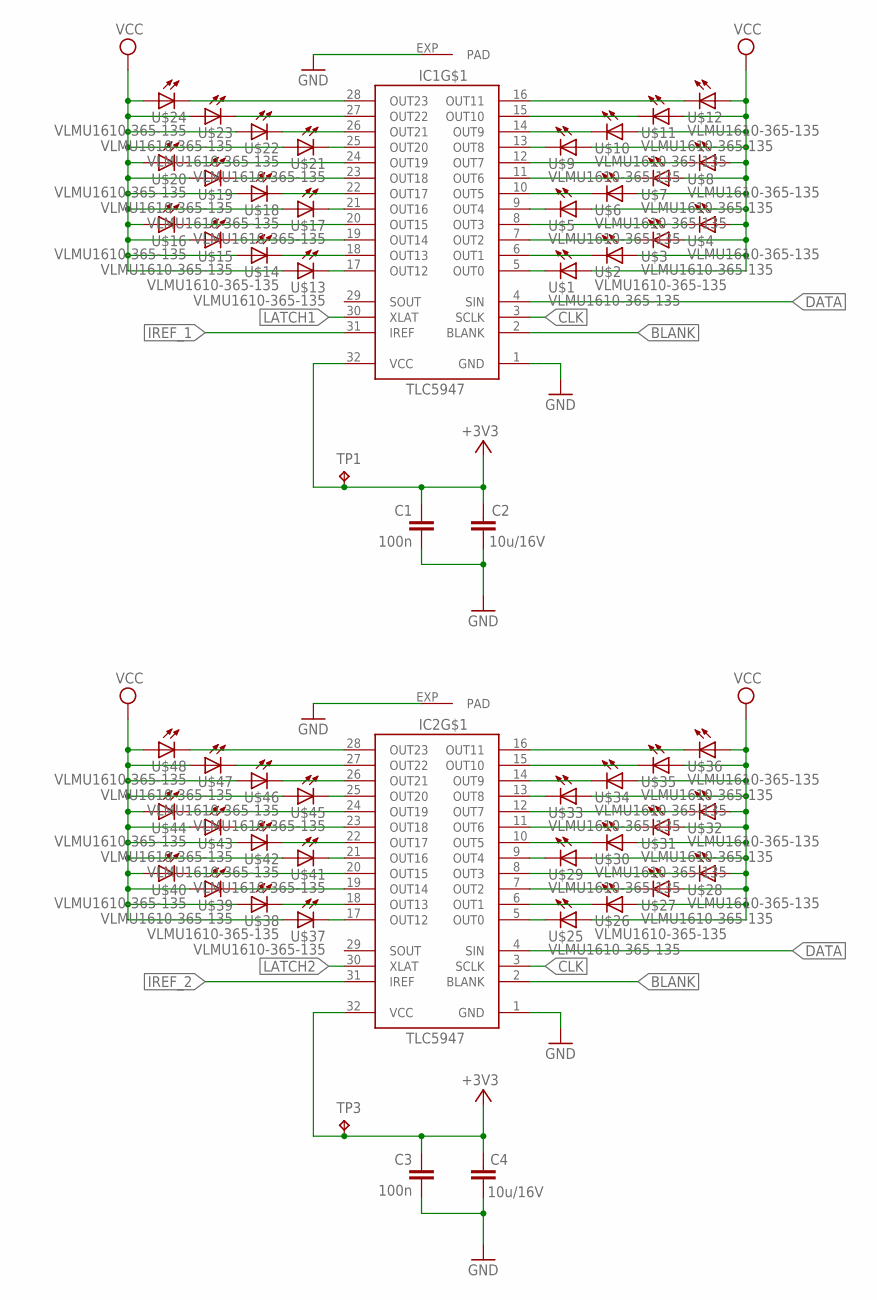
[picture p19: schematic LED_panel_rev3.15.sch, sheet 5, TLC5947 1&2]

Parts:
C1, C3: 100n; C1206K
C2, C4: 10u/16V; C1206K
IC1, IC2: TLC5947-DAP; HTSSOP32DAP
TP1, TP3: TPTP20R; TP20R
U$1, U$2, U$3, U$4, U$5, U$6, U$7, U$8, U$9, U$10, U$11, U$12, U$13, U$14, U$15, U$16, U$17, U$18, U$19, U$20, U$21, U$22, U$23, U$24, U$25, U$26, U$27, U$28, U$29, U$30, U$31, U$32, U$33, U$34, U$35, U$36, U$37, U$38, U$39, U$40, U$41, U$42, U$43, U$44, U$45, U$46, U$47, U$48: VLMU1610-365-135; SMD_CERAMIC_MID_POWER

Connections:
+3V3: C1.2, C2.2, C3.2, C4.2, IC1.32 (VCC), IC2.32 (VCC), TP1.TP, TP3.TP; also elsewhere on the board
BLANK: IC1.2 (BLANK), IC2.2 (BLANK); also elsewhere on the board
CLK: IC1.3 (SCLK), IC2.3 (SCLK); also elsewhere on the board
DATA: IC1.4 (SIN), IC2.4 (SIN); also elsewhere on the board
GND: C1.1, C2.1, C3.1, C4.1, IC1.1 (GND), IC1.EXP (PAD), IC2.1 (GND), IC2.EXP (PAD); also elsewhere on the board
IREF_1: IC1.31 (IREF); also elsewhere on the board
IREF_2: IC2.31 (IREF); also elsewhere on the board
LATCH1: IC1.30 (XLAT); also elsewhere on the board
LATCH2: IC2.30 (XLAT); also elsewhere on the board
unnamed: IC1.28 (OUT23), U$24.P$2 (C)
unnamed: IC1.27 (OUT22), U$23.P$2 (C)
unnamed: IC1.26 (OUT21), U$22.P$2 (C)
unnamed: IC1.25 (OUT20), U$21.P$2 (C)
unnamed: IC1.24 (OUT19), U$20.P$2 (C)
unnamed: IC1.23 (OUT18), U$19.P$2 (C)
unnamed: IC1.22 (OUT17), U$18.P$2 (C)
unnamed: IC1.21 (OUT16), U$17.P$2 (C)
unnamed: IC1.20 (OUT15), U$16.P$2 (C)
unnamed: IC1.19 (OUT14), U$15.P$2 (C)
unnamed: IC1.18 (OUT13), U$14.P$2 (C)
unnamed: IC1.17 (OUT12), U$13.P$2 (C)
unnamed: IC1.16 (OUT11), U$12.P$2 (C)
unnamed: IC1.15 (OUT10), U$11.P$2 (C)
unnamed: IC1.14 (OUT9), U$10.P$2 (C)
unnamed: IC1.13 (OUT8), U$9.P$2 (C)
unnamed: IC1.12 (OUT7), U$8.P$2 (C)
unnamed: IC2.28 (OUT23), U$48.P$2 (C)
unnamed: IC2.27 (OUT22), U$47.P$2 (C)
unnamed: IC1.11 (OUT6), U$7.P$2 (C)
unnamed: IC2.26 (OUT21), U$46.P$2 (C)
unnamed: IC1.10 (OUT5), U$6.P$2 (C)
unnamed: IC2.25 (OUT20), U$45.P$2 (C)
unnamed: IC1.9 (OUT4), U$5.P$2 (C)
unnamed: IC2.24 (OUT19), U$44.P$2 (C)
unnamed: IC1.8 (OUT3), U$4.P$2 (C)
unnamed: IC2.23 (OUT18), U$43.P$2 (C)
unnamed: IC1.7 (OUT2), U$3.P$2 (C)
unnamed: IC2.22 (OUT17), U$42.P$2 (C)
unnamed: IC1.6 (OUT1), U$2.P$2 (C)
unnamed: IC2.21 (OUT16), U$41.P$2 (C)
unnamed: IC1.5 (OUT0), U$1.P$2 (C)
unnamed: IC2.20 (OUT15), U$40.P$2 (C)
unnamed: IC2.19 (OUT14), U$39.P$2 (C)
unnamed: IC2.18 (OUT13), U$38.P$2 (C)
unnamed: IC2.17 (OUT12), U$37.P$2 (C)
unnamed: IC2.16 (OUT11), U$36.P$2 (C)
unnamed: IC2.15 (OUT10), U$35.P$2 (C)
unnamed: IC2.14 (OUT9), U$34.P$2 (C)
unnamed: IC2.13 (OUT8), U$33.P$2 (C)
unnamed: IC2.12 (OUT7), U$32.P$2 (C)
unnamed: IC2.11 (OUT6), U$31.P$2 (C)
unnamed: IC2.10 (OUT5), U$30.P$2 (C)
unnamed: IC2.9 (OUT4), U$29.P$2 (C)
unnamed: IC2.8 (OUT3), U$28.P$2 (C)
unnamed: IC2.7 (OUT2), U$27.P$2 (C)
unnamed: IC2.6 (OUT1), U$26.P$2 (C)
unnamed: IC2.5 (OUT0), U$25.P$2 (C)
VCC: U$1.P$1 (A), U$2.P$1 (A), U$3.P$1 (A), U$4.P$1 (A), U$5.P$1 (A), U$6.P$1 (A), U$7.P$1 (A), U$8.P$1 (A), U$9.P$1 (A), U$10.P$1 (A), U$11.P$1 (A), U$12.P$1 (A), U$13.P$1 (A), U$14.P$1 (A), U$15.P$1 (A), U$16.P$1 (A), U$17.P$1 (A), U$18.P$1 (A), U$19.P$1 (A), U$20.P$1 (A), U$21.P$1 (A), U$22.P$1 (A), U$23.P$1 (A), U$24.P$1 (A), U$25.P$1 (A), U$26.P$1 (A), U$27.P$1 (A), U$28.P$1 (A), U$29.P$1 (A), U$30.P$1 (A), U$31.P$1 (A), U$32.P$1 (A), U$33.P$1 (A), U$34.P$1 (A), U$35.P$1 (A), U$36.P$1 (A), U$37.P$1 (A), U$38.P$1 (A), U$39.P$1 (A), U$40.P$1 (A), U$41.P$1 (A), U$42.P$1 (A), U$43.P$1 (A), U$44.P$1 (A), U$45.P$1 (A), U$46.P$1 (A), U$47.P$1 (A), U$48.P$1 (A); also elsewhere on the board

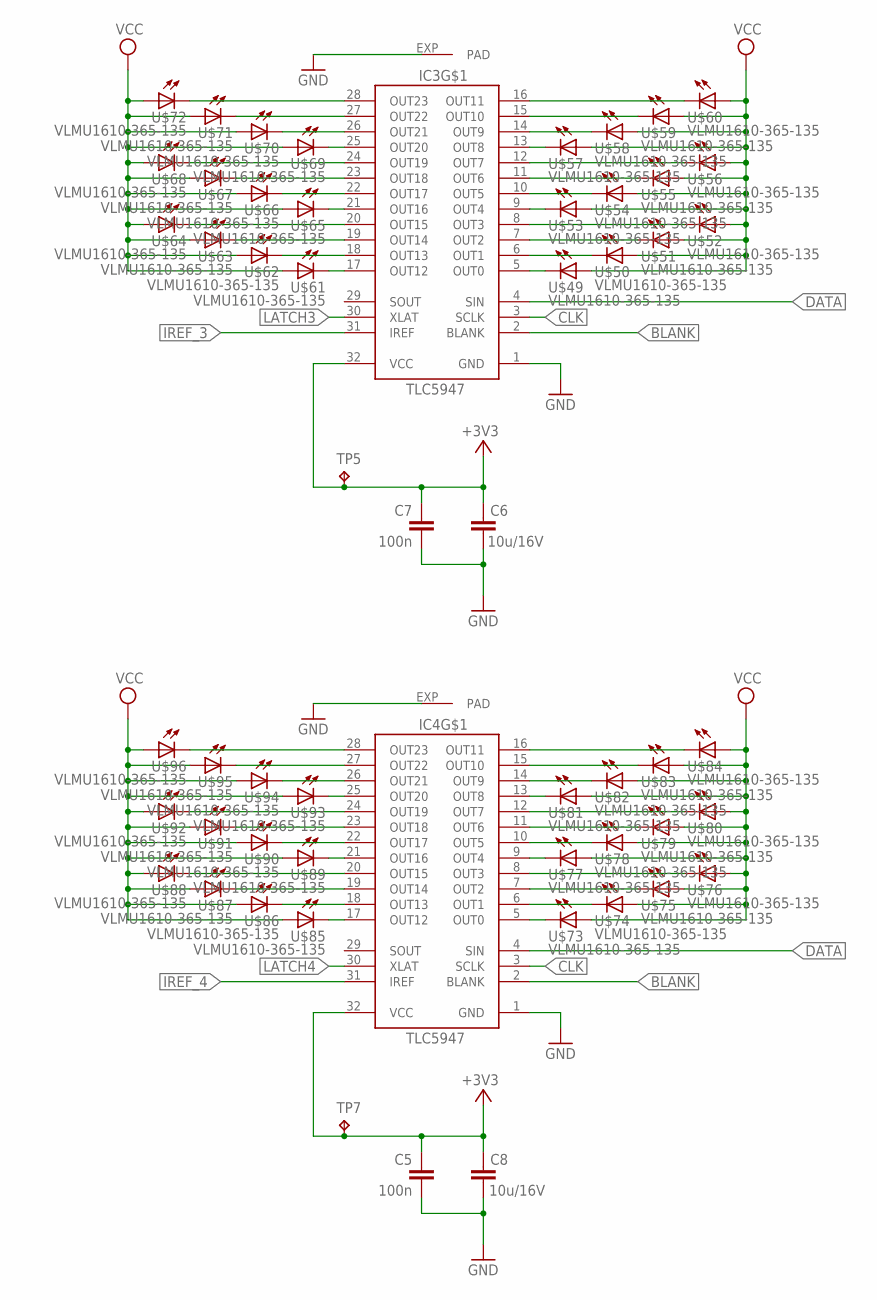
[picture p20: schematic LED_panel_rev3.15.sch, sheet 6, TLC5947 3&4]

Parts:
C5, C7: 100n; C1206K
C6, C8: 10u/16V; C1206K
IC3, IC4: TLC5947-DAP; HTSSOP32DAP
TP5, TP7: TPTP20R; TP20R
U$49, U$50, U$51, U$52, U$53, U$54, U$55, U$56, U$57, U$58, U$59, U$60, U$61, U$62, U$63, U$64, U$65, U$66, U$67, U$68, U$69, U$70, U$71, U$72, U$73, U$74, U$75, U$76, U$77, U$78, U$79, U$80, U$81, U$82, U$83, U$84, U$85, U$86, U$87, U$88, U$89, U$90, U$91, U$92, U$93, U$94, U$95, U$96: VLMU1610-365-135; SMD_CERAMIC_MID_POWER

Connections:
+3V3: C5.2, C6.2, C7.2, C8.2, IC3.32 (VCC), IC4.32 (VCC), TP5.TP, TP7.TP; also elsewhere on the board
BLANK: IC3.2 (BLANK), IC4.2 (BLANK); also elsewhere on the board
CLK: IC3.3 (SCLK), IC4.3 (SCLK); also elsewhere on the board
DATA: IC3.4 (SIN), IC4.4 (SIN); also elsewhere on the board
GND: C5.1, C6.1, C7.1, C8.1, IC3.1 (GND), IC3.EXP (PAD), IC4.1 (GND), IC4.EXP (PAD); also elsewhere on the board
IREF_3: IC3.31 (IREF); also elsewhere on the board
IREF_4: IC4.31 (IREF); also elsewhere on the board
LATCH3: IC3.30 (XLAT); also elsewhere on the board
LATCH4: IC4.30 (XLAT); also elsewhere on the board
unnamed: IC3.28 (OUT23), U$72.P$2 (C)
unnamed: IC3.27 (OUT22), U$71.P$2 (C)
unnamed: IC3.26 (OUT21), U$70.P$2 (C)
unnamed: IC3.25 (OUT20), U$69.P$2 (C)
unnamed: IC3.24 (OUT19), U$68.P$2 (C)
unnamed: IC3.23 (OUT18), U$67.P$2 (C)
unnamed: IC3.22 (OUT17), U$66.P$2 (C)
unnamed: IC3.21 (OUT16), U$65.P$2 (C)
unnamed: IC3.20 (OUT15), U$64.P$2 (C)
unnamed: IC3.19 (OUT14), U$63.P$2 (C)
unnamed: IC3.18 (OUT13), U$62.P$2 (C)
unnamed: IC3.17 (OUT12), U$61.P$2 (C)
unnamed: IC3.16 (OUT11), U$60.P$2 (C)
unnamed: IC3.15 (OUT10), U$59.P$2 (C)
unnamed: IC3.14 (OUT9), U$58.P$2 (C)
unnamed: IC3.13 (OUT8), U$57.P$2 (C)
unnamed: IC3.12 (OUT7), U$56.P$2 (C)
unnamed: IC3.11 (OUT6), U$55.P$2 (C)
unnamed: IC3.10 (OUT5), U$54.P$2 (C)
unnamed: IC3.9 (OUT4), U$53.P$2 (C)
unnamed: IC3.8 (OUT3), U$52.P$2 (C)
unnamed: IC3.7 (OUT2), U$51.P$2 (C)
unnamed: IC3.6 (OUT1), U$50.P$2 (C)
unnamed: IC3.5 (OUT0), U$49.P$2 (C)
unnamed: IC4.28 (OUT23), U$96.P$2 (C)
unnamed: IC4.27 (OUT22), U$95.P$2 (C)
unnamed: IC4.26 (OUT21), U$94.P$2 (C)
unnamed: IC4.25 (OUT20), U$93.P$2 (C)
unnamed: IC4.24 (OUT19), U$92.P$2 (C)
unnamed: IC4.23 (OUT18), U$91.P$2 (C)
unnamed: IC4.22 (OUT17), U$90.P$2 (C)
unnamed: IC4.21 (OUT16), U$89.P$2 (C)
unnamed: IC4.20 (OUT15), U$88.P$2 (C)
unnamed: IC4.19 (OUT14), U$87.P$2 (C)
unnamed: IC4.18 (OUT13), U$86.P$2 (C)
unnamed: IC4.17 (OUT12), U$85.P$2 (C)
unnamed: IC4.16 (OUT11), U$84.P$2 (C)
unnamed: IC4.15 (OUT10), U$83.P$2 (C)
unnamed: IC4.14 (OUT9), U$82.P$2 (C)
unnamed: IC4.13 (OUT8), U$81.P$2 (C)
unnamed: IC4.12 (OUT7), U$80.P$2 (C)
unnamed: IC4.11 (OUT6), U$79.P$2 (C)
unnamed: IC4.10 (OUT5), U$78.P$2 (C)
unnamed: IC4.9 (OUT4), U$77.P$2 (C)
unnamed: IC4.8 (OUT3), U$76.P$2 (C)
unnamed: IC4.7 (OUT2), U$75.P$2 (C)
unnamed: IC4.6 (OUT1), U$74.P$2 (C)
unnamed: IC4.5 (OUT0), U$73.P$2 (C)
VCC: U$49.P$1 (A), U$50.P$1 (A), U$51.P$1 (A), U$52.P$1 (A), U$53.P$1 (A), U$54.P$1 (A), U$55.P$1 (A), U$56.P$1 (A), U$57.P$1 (A), U$58.P$1 (A), U$59.P$1 (A), U$60.P$1 (A), U$61.P$1 (A), U$62.P$1 (A), U$63.P$1 (A), U$64.P$1 (A), U$65.P$1 (A), U$66.P$1 (A), U$67.P$1 (A), U$68.P$1 (A), U$69.P$1 (A), U$70.P$1 (A), U$71.P$1 (A), U$72.P$1 (A), U$73.P$1 (A), U$74.P$1 (A), U$75.P$1 (A), U$76.P$1 (A), U$77.P$1 (A), U$78.P$1 (A), U$79.P$1 (A), U$80.P$1 (A), U$81.P$1 (A), U$82.P$1 (A), U$83.P$1 (A), U$84.P$1 (A), U$85.P$1 (A), U$86.P$1 (A), U$87.P$1 (A), U$88.P$1 (A), U$89.P$1 (A), U$90.P$1 (A), U$91.P$1 (A), U$92.P$1 (A), U$93.P$1 (A), U$94.P$1 (A), U$95.P$1 (A), U$96.P$1 (A); also elsewhere on the board

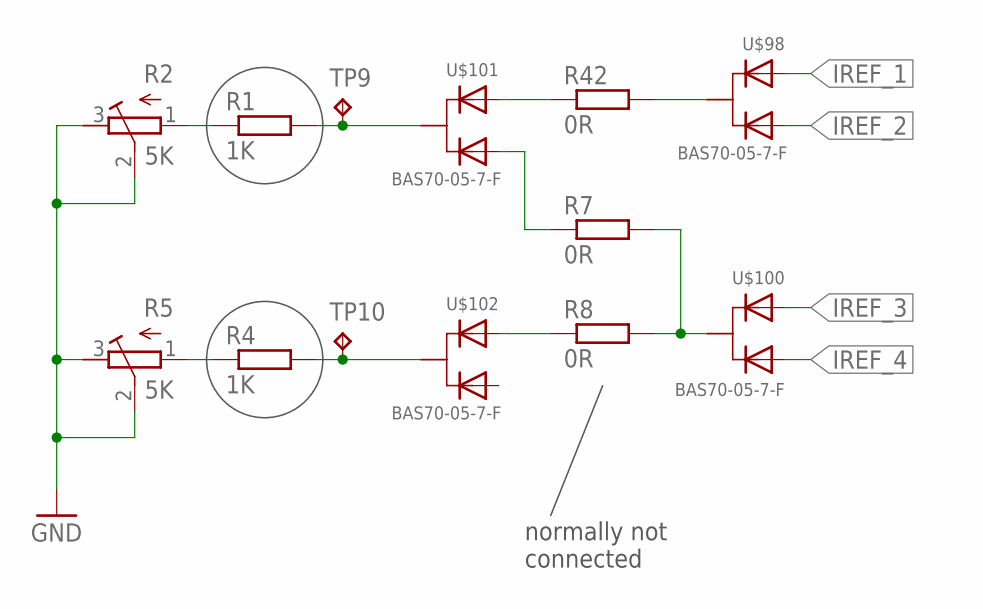
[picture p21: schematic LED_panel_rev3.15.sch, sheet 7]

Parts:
R1, R4: 1K; R1206
R2, R5: 5K; RTRIM4G/J
R7, R8, R42: 0R; R1206
TP9, TP10: TPTP20R; TP20R
U$98, U$100, U$101, U$102: BAS70-05-7-F; SOT23

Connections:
GND: R2.2 (S), R2.3 (E), R5.2 (S), R5.3 (E); also elsewhere on the board
IREF_1: U$98.2 (B); also elsewhere on the board
IREF_1&2: R42.2, U$98.3 (C)
IREF_2: U$98.1 (A); also elsewhere on the board
IREF_3: U$100.2 (B); also elsewhere on the board
IREF_3&4: R7.2, R8.2, U$100.3 (C)
IREF_4: U$100.1 (A); also elsewhere on the board
unnamed: R1.1, R2.1 (A)
unnamed: R4.1, R5.1 (A)
unnamed: R1.2, TP9.TP, U$101.3 (C)
unnamed: R4.2, TP10.TP, U$102.3 (C)
unnamed: R42.1, U$101.2 (B)
unnamed: R7.1, U$101.1 (A)
unnamed: R8.1, U$102.2 (B)

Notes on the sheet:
normally not connected

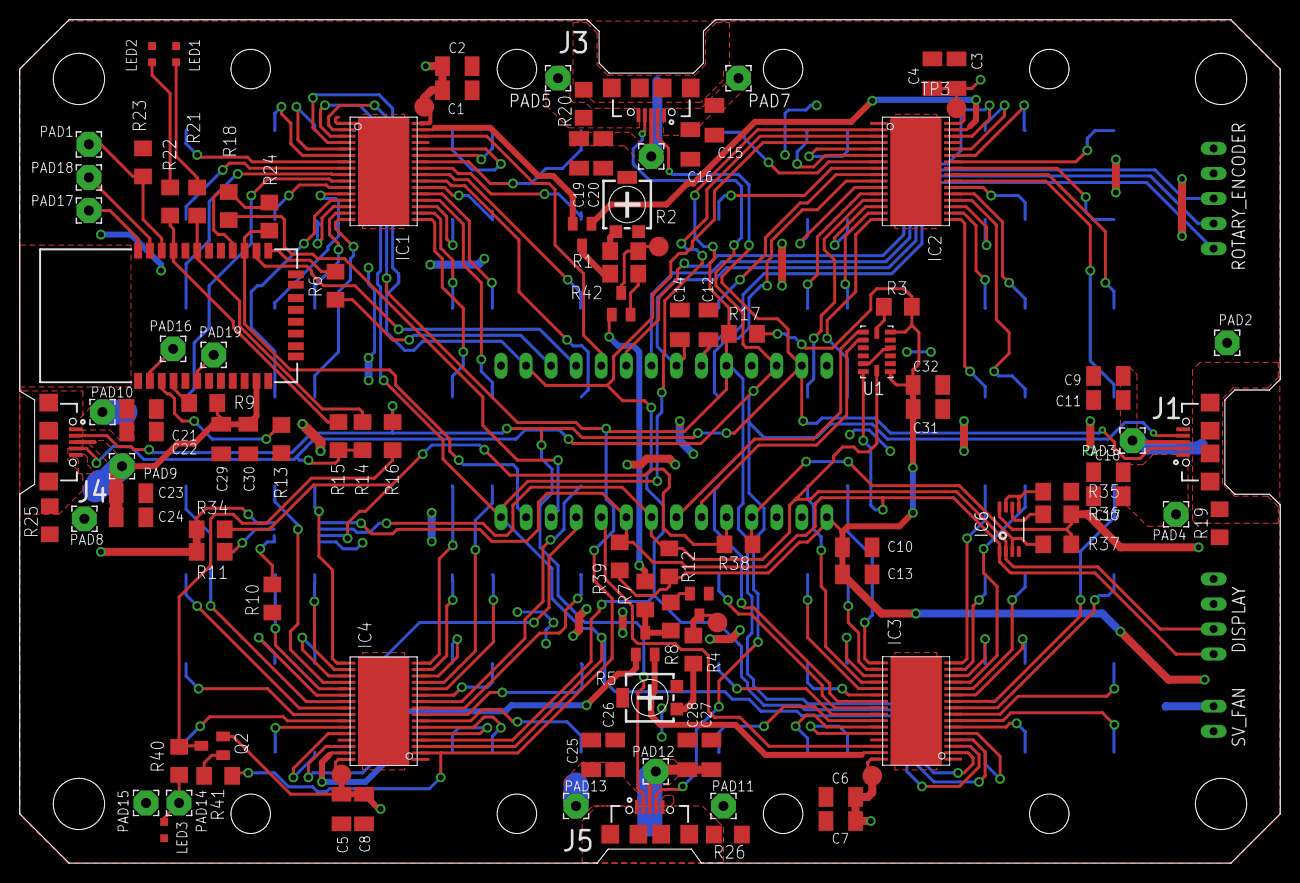
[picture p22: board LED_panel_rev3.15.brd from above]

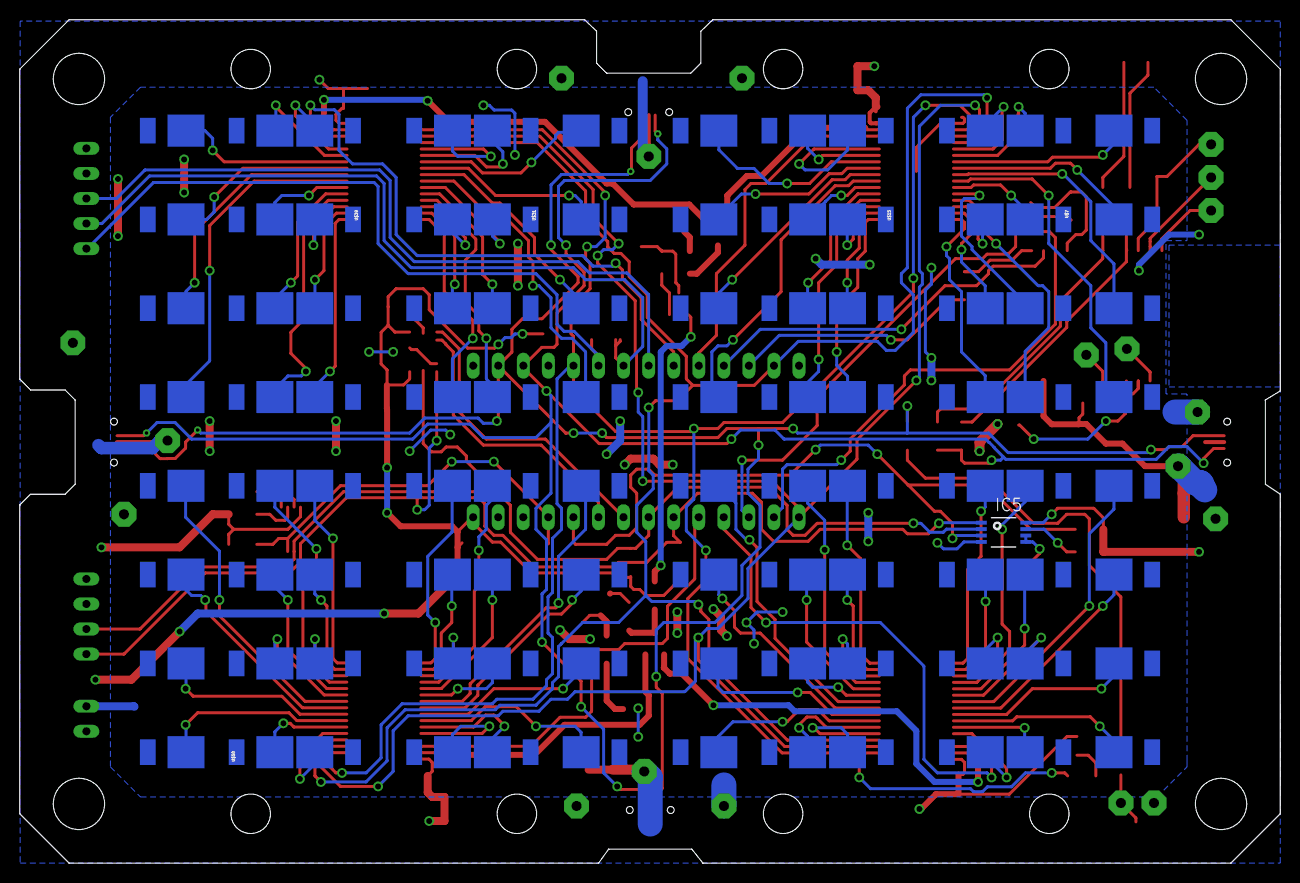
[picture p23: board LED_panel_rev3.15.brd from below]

Board: 2 copper layers, 127.8 x 85.5 mm, 214 parts (97 on the bottom side), 159 nets.

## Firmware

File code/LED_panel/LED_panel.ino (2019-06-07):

#include "Bielefeld-CeBiTec_LED_panel.h"

// display
#include <Adafruit_GFX.h>
#include <Adafruit_SSD1306.h>

// bluetooth
#include <avr/pgmspace.h>
#include <SoftwareSerial.h>

// C Strings
#include <stdio.h>
#include <ctype.h>

// temperature sensors
#include <Wire.h>
#include "Adafruit_MCP9808.h"

// acceleration sensor
#include <Adafruit_Sensor.h>
#include <Adafruit_ADXL345_U.h>

// rotary encoder
#define RE_CLK 4 //2
#define RE_DT 5//4
#define RE_SW 6

// HC-05/HC-06 bluetooth module
#define TXD 9
#define RXD 10

// tilt switch
#define TILT_SW 2
#define UPSIDE_UP 0
#define UPSIDE_DOWN 2

// Program Sequence
#define MAX_ENTRIES 30
#define ENTRY_LENGTH 38
#define CONSTANT 	0
#define LINEAR 		1
#define EXPONENTIAL 2
#define JUMP 		4
//#define LOGARITHMIC 3
#define BT_NOTHING 	0
#define BT_NEW_PROGRAM 1
#define BT_STOP 2
#define BT_ERROR 3
#define BT_CANCEL 4
#define BT_PING 5
#define UPDATE_INTERVAL 2

//display
// I2C ports!
#define OLED_RESET 2 // nicht genutzt bei diesem Display

//others
#define BLANK	 	3

// iGEM Bielefeld-CeBiTec 2017 logo
const uint8_t logo[8129] PROGMEM = {
0x0,0x0,0x0,0xf,0xc0,0x0,0x0,0x0,0x0,0x0,0x0,0x0,0x0,0x0,0x0,0x0,
0x0,0x0,0x0,0x1f,0xe0,0x0,0x0,0x0,0x0,0x0,0x0,0x0,0x0,0x0,0x0,0x0,
0x0,0x0,0x0,0x1f,0xe0,0x0,0x0,0x0,0x0,0x0,0x0,0x0,0x0,0x0,0x0,0x0,
0x0,0x0,0x0,0x1f,0xe0,0x0,0x0,0x0,0x0,0x0,0x0,0x0,0x0,0x0,0x0,0x0,
0x0,0x0,0x0,0x1f,0xe0,0x0,0x0,0x0,0x0,0x0,0x0,0x0,0x0,0x0,0x0,0x0,
0x0,0x0,0x0,0xf,0xc0,0x0,0x0,0x0,0x0,0x0,0x0,0x0,0x0,0x0,0x0,0x0,
0x0,0x0,0x0,0x7,0x80,0x0,0x0,0x0,0x0,0x0,0x0,0x0,0x0,0x0,0x0,0x0,
0x0,0x0,0x0,0x0,0x0,0x3,0xc0,0x0,0x0,0x0,0x0,0x0,0x0,0x0,0x0,0x0,
0x0,0x0,0x0,0xf,0xe0,0x3f,0xfc,0x1f,0xff,0xf7,0xf0,0x7,0xf0,0x0,0x0,0x0,
0x0,0x0,0x0,0x19,0xb0,0x7f,0xff,0x1f,0xff,0xf7,0xfc,0x1f,0xf0,0x0,0x0,0x0,
0x0,0x0,0x0,0x1b,0x1,0xff,0xff,0x9f,0xff,0xf7,0xfc,0x1f,0xf0,0x0,0x0,0x0,
0x0,0x0,0x0,0x16,0xf3,0xff,0xff,0x9f,0xff,0xf7,0xfc,0x1f,0xf0,0x0,0x0,0x0,
0x0,0x0,0x0,0x18,0x3,0xf8,0x1f,0x9f,0x80,0x7,0xfe,0x3f,0xf0,0x0,0x0,0x0,
0x0,0x0,0x0,0x1d,0xd7,0xf0,0x0,0x1f,0x80,0x7,0xfe,0x3f,0xf0,0x0,0x0,0x0,
0x0,0x0,0x0,0x16,0x37,0xf0,0x0,0x1f,0x80,0x7,0xfe,0x3f,0xf0,0x0,0x0,0x0,
0x0,0x0,0x0,0x13,0xc7,0xe0,0xff,0x9f,0xff,0xf7,0xde,0x3f,0xf0,0x0,0x0,0x0,
0x0,0x0,0x0,0x11,0xa7,0xe0,0xff,0xdf,0xff,0xf7,0xdf,0x7f,0xf0,0x0,0x0,0x0,
0x0,0x0,0x0,0x12,0x17,0xe0,0xff,0xdf,0xff,0xf7,0xcf,0x79,0xf0,0x0,0x0,0x0,
0x0,0x0,0x0,0x15,0xc7,0xe0,0xff,0xdf,0xff,0xf7,0xcf,0xf9,0xf0,0x0,0x0,0x0,
0x0,0x0,0x0,0x1c,0x17,0xf0,0x3,0xdf,0x80,0x7,0xcf,0xf9,0xf0,0x0,0x0,0x0,
0x0,0x0,0x0,0x1b,0xb7,0xf0,0x7,0xdf,0x80,0x7,0xcf,0xf9,0xf0,0x0,0x0,0x0,
0x0,0x0,0x0,0x14,0x63,0xf8,0xf,0xdf,0x80,0x7,0xc7,0xf1,0xf0,0x0,0x0,0x0,
0x0,0x0,0x0,0x13,0x43,0xff,0xff,0xdf,0xff,0xf7,0xc7,0xf1,0xf0,0x0,0x0,0x0,
0x0,0x0,0x0,0x19,0xd1,0xff,0xff,0x9f,0xff,0xf7,0xc3,0xe1,0xf0,0x0,0x0,0x0,
0x0,0x0,0x0,0x1f,0xf0,0x7f,0xff,0x1f,0xff,0xf7,0xc3,0xe1,0xf0,0x0,0x0,0x0,
0x0,0x0,0x0,0x3a,0xb8,0x3f,0xfc,0x1f,0xff,0xf7,0xc3,0xe1,0xf0,0x0,0x0,0x0,
0x0,0x0,0x0,0x37,0xe8,0x0,0x0,0x0,0x0,0x0,0x0,0x0,0x0,0x0,0x0,0x0,
0x0,0x0,0x0,0x1f,0xf3,0xed,0xd8,0xf7,0xbd,0x8e,0x1c,0xe2,0xf0,0x0,0x0,0x0,
0x0,0x0,0x0,0x1f,0xf3,0x2d,0x18,0xc6,0x31,0x89,0x16,0xa6,0x30,0x0,0x0,0x0,
0x0,0x0,0x0,0x1f,0xf3,0xed,0x98,0xe7,0xb9,0x89,0x4,0xaa,0x20,0x0,0x0,0x0,
0x0,0x0,0x0,0x1f,0xf3,0x2d,0x18,0xc6,0x31,0x89,0x8,0xa2,0x60,0x0,0x0,0x0,
0x0,0x0,0x0,0x1f,0xf3,0xed,0xde,0xf6,0x3d,0xee,0x1e,0xe2,0xc0,0x0,0x0,0x0
};

// Progam Sequence
struct Entry {
   unsigned short int		slope;
   unsigned short int		gradient;
   unsigned long int		millis;
   unsigned short int		left_0;
   unsigned short int		right_0;
   unsigned short int		left_1;
   unsigned short int		right_1;

   unsigned short int 		acceleration;
   double					accel;
   unsigned long int 		accel_millis;

   unsigned int				ledBuffer[12];
   unsigned long int   		runtime;
   unsigned long int    	start_time;
   unsigned short int 		c;
   double					x;
   unsigned short int 		c_r;
   double					x_r;

   unsigned short int 		jump_index;
   unsigned short int 		remaining_jumps;
};
int entryCounter = 0;
struct Entry programSequence[MAX_ENTRIES];
int bt_code = 0;
int currentEntry = -1;
//int intensity;
char btBuffer[ENTRY_LENGTH*(MAX_ENTRIES+1)+1];
int curPos = 0;

// create LED panel object
LED_panel led_panel = LED_panel();
unsigned short blank_state;

// rotary encoder states
int rot_clk;
int lst_rot_clk;
unsigned int reValue;
unsigned int intensity;
unsigned long int sw_pressed;
unsigned int time_inten;
unsigned long int time_end;

// timing
unsigned long int last_checked;
unsigned long int tmp_sensor_last_update;
unsigned long int acc_sensor_last_update;
unsigned long int last_accel_exceed;
unsigned int tmp_sensor_update_interval;
unsigned int acc_sensor_update_interval;
unsigned long int time_reference;

// display
Adafruit_SSD1306 display(OLED_RESET);

// temperature sensors
Adafruit_MCP9808 tempsensor_btm = Adafruit_MCP9808();
Adafruit_MCP9808 tempsensor_top = Adafruit_MCP9808();
#define TMP_BTM 0b0011001
#define TMP_TOP 0b0011010

// acceleration sensor
Adafruit_ADXL345_Unified accel = Adafruit_ADXL345_Unified(12345);
float last_x;
float last_y;
float last_z;
float absdiff_x;
float absdiff_y;
float absdiff_z;
float min_rel_acc_diff;
float last_accel_exceed_value;
float max_last_accel_exceed_value;
unsigned short int orientation;
uint32_t accel_exceed_buffer;
#define ACCEL_EXEED_BUFFER_DEFAULT_VALUE 0
#define MIN_REL_ACC_DIFF 1.0
#define TMP_SENSOR_UPDATE_INTERVAL 500
#define ACC_SENSOR_UPDATE_INTERVAL 30

#define MIN_EXEEDINGS 12
#define N_MEASUREMENTS 32

// bluetooth serial communication
SoftwareSerial btSerial(TXD, RXD);

void setup() {
	time_reference = millis();

	bt_code = 0;
	currentEntry = -1;

	// USB Serial
	Serial.begin(9600);
	//Serial.println("Thanks for using the LED panel build by the iGEM Team Bielefeld-CeBiTec 2017!");
	//Serial.println("Please write to mhaak@cebitec.uni-bielefeld.de in case of any questions regarding this product.");

	// bluetooth setup
	btSerial.begin(9600);
	btSerial.println("bluetooth available");

	// led-panel setup
	led_panel.begin();
	led_panel.setPWM(0);
	blank_state = 1;

	// rotary encoder setup
	pinMode(RE_SW, INPUT);
	pinMode(RE_CLK, INPUT);
	pinMode(RE_DT, INPUT);
	attachInterrupt(digitalPinToInterrupt(RE_CLK), irupt_re_clk, CHANGE);
	attachInterrupt(digitalPinToInterrupt(RE_SW), irupt_re_sw, CHANGE);
	lst_rot_clk = digitalRead(RE_CLK);
	intensity = 100;
	time_inten = 1;

	// temperature sensor setup
	if (!tempsensor_btm.begin(TMP_BTM) or !tempsensor_top.begin(TMP_TOP)) {
		//Serial.println("Couldn't find MCP9808!");
		while (1);
	}
	tmp_sensor_last_update = millis();

	// acceleration sensor
	if(!accel.begin())
	{
		/* There was a problem detecting the ADXL345 ... check your connections */
		//Serial.println("Ooops, no ADXL345 detected ... Check your wiring!");
		while(1);
	}
	accel.setRange(ADXL345_RANGE_16_G);
	accel.setDataRate(ADXL345_DATARATE_3200_HZ);
	sensors_event_t event; 
	accel.getEvent(&event);
	last_x = event.acceleration.x;
	last_y = event.acceleration.y;
	last_z = event.acceleration.z;
	absdiff_x = 0.0;
	absdiff_y = 0.0;
	absdiff_z = 0.0;
	max_last_accel_exceed_value = 0.0;
	tmp_sensor_update_interval = TMP_SENSOR_UPDATE_INTERVAL;
	acc_sensor_update_interval = ACC_SENSOR_UPDATE_INTERVAL;
	accel_exceeds_buffer = ACCEL_EXEED_BUFFER_DEFAULT_VALUE;

	min_rel_acc_diff = MIN_REL_ACC_DIFF;

	// initialize display with the I2C addr 0x3C
	display.begin(SSD1306_SWITCHCAPVCC, 0x3C);
	display.clearDisplay();
	display.setTextColor(WHITE);
	display.drawBitmap(0, 0, logo, 128, 32, 1);
	display.display();

	// orientation
	sensor_update();
	display.setRotation(orientation);

	// FUNCTION TEST
	// digitalWrite(BLANK, LOW);
	// blank_state = 0;
	// led_panel.setPWM(200);
	// delay(500);
	// led_panel.setPWM(0);
	// unsigned short int test_gadient[12] = {100, 200, 300, 400, 500, 600, 700, 800, 900, 1000, 1100, 1200};
	// led_panel.testGradient(test_gadient);
	// digitalWrite(BLANK, HIGH);
	// blank_state = 1;	
}

void loop(){
	noInterrupts();

	if(currentEntry == -1){
		switch (checkBluetoothForProgram()){
			case BT_NEW_PROGRAM:
				//Serial.println("new program received!");
				//Serial.println(btBuffer);
				
				if(makeProgram()){
					//Serial.println("made program");
					printProgram();
					startProgram();
				}else{
					//Serial.println("ERR: bluetooth transmission not successful");
					bt_send("  program corrupted");
				}
				break;
			case BT_ERROR:
				//Serial.println("Error occured while reading btSerial!");
				bt_send("  program corrupted");
				break;
			case BT_PING:
				//Serial.println("Received ping order.");
				bt_send("  P");
				break;
			default:
				break;
		}
	}
	else{
		switch(checkBluetoothForOrder()){
			case BT_CANCEL:
				//Serial.println("Received order to cancel program.");
				stopProgram();
				break;
			case BT_PING:
				//Serial.println("Received ping order.");
				btSerial.println("  P"); // no bt_send, as interrupts shall not occur during program execution
				break;
			default:
				break;
		}
	}
	
	interrupts();

	if(currentEntry >= 0){
		if ((millis() - last_checked) > UPDATE_INTERVAL){
			last_checked = millis();
			if((updateLEDs(currentEntry)) == 0){
				currentEntry++;
				// reset accel_exceeds_buffer
				accel_exceeds_buffer = ACCEL_EXEED_BUFFER_DEFAULT_VALUE;

				//Serial.println(currentEntry);
				// handle jumps
				while (programSequence[currentEntry].slope == JUMP && currentEntry >= 0){
					if (programSequence[currentEntry].remaining_jumps == 0){
						currentEntry++;
						//Serial.println(currentEntry);
						break;
					}else{
						programSequence[currentEntry].remaining_jumps--;
						//Serial.println(currentEntry);
						Serial.print("jumps remaining: ");
						//Serial.println(programSequence[currentEntry].remaining_jumps);
						currentEntry = programSequence[currentEntry].jump_index;
					}
				}

				if((currentEntry < entryCounter) && (currentEntry >= 0)){
					programSequence[currentEntry].start_time = millis();
					updateLEDs(currentEntry);
				}
				else{
					stopProgram();
				}
			}
		}
	}
	else if(currentEntry == -2){
		if(millis() >= time_end)stopProgram();
	}

	update_display();
	sensor_update();
}

int sum_accel_exceedings(uint32_t buffer, uint16_t n_measurements)
{
	uint32_t num_bits = 0;
	if(buffer){
		for(unsigned int i=0; i<n_measurements; i++){
			if (buffer & 1) num_bits ++;
			buffer>>=1;
		}
	}
	return num_bits;
}
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

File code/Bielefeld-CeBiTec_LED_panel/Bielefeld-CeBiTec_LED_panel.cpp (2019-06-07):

#include <Bielefeld-CeBiTec_LED_panel.h>

uint16_t ledOrder[6][4] = {{2,3,4,5},
						  {1,6,7,8},
						  {0,9,10,11},
						  {23,14,13,12},
						  {22,17,16,15},
						  {21,20,19,18}};

TLC5947::TLC5947(uint8_t c, uint8_t d, uint8_t l) {
	_clk = c;
	_dat = d;
	_lat = l;

	pwmbuffer = (uint16_t *)malloc(2 * 24);
	memset(pwmbuffer, 0, 2*24);
}

LED_panel::LED_panel() {
	uint8_t c = 13;
	uint8_t d = 11;
	uint8_t b = 3;
	uint8_t l1 = 8;
	uint8_t l2 = 16;
	uint8_t l3 = 7;
	uint8_t l4 = 17;
	_tlcs[0] = new TLC5947(c, d, l1);
	_tlcs[1] = new TLC5947(c, d, l2);
	_tlcs[2] = new TLC5947(c, d, l3);
	_tlcs[3] = new TLC5947(c, d, l4);

	blank = b;
}

void TLC5947::write(void) {
	digitalWrite(_lat, LOW);
	// 24 channels per TLC5947
	for (int16_t c=23; c >= 0 ; c--) {
		// 12 bits per channel, send MSB first
		for (int8_t b=11; b>=0; b--) {
			digitalWrite(_clk, LOW);
			if (pwmbuffer[c] & (1 << b)) 
				digitalWrite(_dat, HIGH);
			else digitalWrite(_dat, LOW);
			digitalWrite(_clk, HIGH);
		}
	}
	digitalWrite(_clk, LOW);
	digitalWrite(_lat, HIGH);	
	digitalWrite(_lat, LOW);
}

void TLC5947::setPWM(uint16_t chan, uint16_t pwm) {
	if (pwm > 4095) pwm = 4095;
	if (chan > 24) return;
	pwmbuffer[chan] = pwm;	
}


boolean TLC5947::begin() {
	if (!pwmbuffer) return false;
	pinMode(_clk, OUTPUT);
	pinMode(_dat, OUTPUT);
	pinMode(_lat, OUTPUT);
	digitalWrite(_lat, LOW);
	return true;
}

void LED_panel::setPWM(uint16_t pwm){
	for (int16_t c=0 ; c <4 ; c++){
		for (int16_t l=23; l >= 0 ; l--){
			_tlcs[c]->setPWM(l, pwm);
		}
		_tlcs[c]->write();
	}
}

void LED_panel::setGradient(unsigned short int pwm[12]){
	for (int16_t c=0 ; c <4 ; c+=2){
		for (int16_t l=0; l < 6 ; l++){
			for (int16_t o=0; o < 4; o++){
				_tlcs[c]->setPWM(ledOrder[l][o], pwm[l + ((c/2)*6)] );
				_tlcs[c+1]->setPWM(ledOrder[5-l][o], pwm[l + ((c/2)*6)] );
			}
		}
		_tlcs[c]->write();
		_tlcs[c+1]->write();
	}
}

void LED_panel::testGradient(unsigned short int pwm[12]){
	for (int16_t c=0 ; c <4 ; c+=2){
		for (int16_t l=0; l < 6 ; l++){
			for (int16_t o=0; o < 4; o++){
				_tlcs[c]->setPWM(ledOrder[l][o], pwm[l + ((c/2)*6)] );
				_tlcs[c+1]->setPWM(ledOrder[5-l][o], pwm[l + ((c/2)*6)] );
			}
			_tlcs[c]->write();
			_tlcs[c+1]->write();
			delay(200);
		}
		_tlcs[c]->write();
	}
}

boolean LED_panel::begin(){
	pinMode(blank, OUTPUT);
	digitalWrite(blank, HIGH);

	for (int16_t c=0 ; c <4 ; c++){
		if (!(_tlcs[c]->begin())) return false;
	}
	return true;
}
